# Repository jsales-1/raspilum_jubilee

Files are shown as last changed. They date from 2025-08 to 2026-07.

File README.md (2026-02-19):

## Science Jubilee

<p align="justify">
Science Jubilee é uma plataforma de automação laboratorial de código aberto, baseada no sistema Jubilee, uma plataforma de movimento multiferramenta extensível, originalmente projetada como uma impressora 3D com troca automática de cabeças de ferramenta <a href="https://jubilee3d.com/index.php?title=Main_Page">[1]</a>.
</p>

<p align="center">
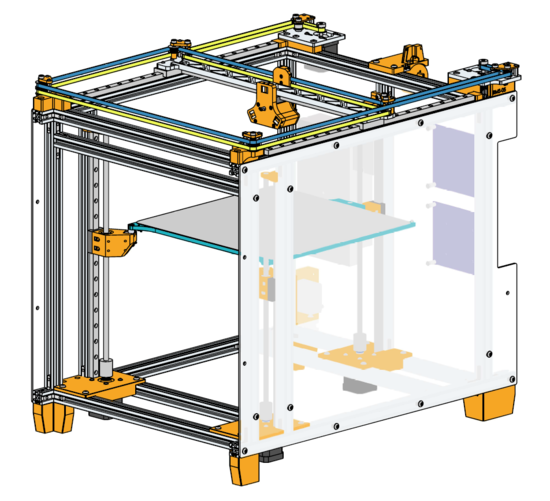
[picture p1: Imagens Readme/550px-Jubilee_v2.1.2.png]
  <br>
  <em>Figura 1 – Representação da estrutura da plataforma Jubilee 3D. </em>
</p>

<p align="justify">
A science-jubilee adapta essa infraestrutura para aplicações científicas, permitindo automação de experimentos com ferramentas como pipetas, câmeras, sondas e manuseio de amostras. A documentação oficial está disponível no site Science Jubilee Docs, que reúne guias de início rápido, construção da plataforma, desenvolvimento, referências da API e contribuições da comunidade. A plataforma é flexível e serve como base para diferentes aplicações de automação laboratorial, desde pipetagem e manipulação de amostras até aquisição de imagens. <a href="https://science-jubilee.readthedocs.io/en/latest/index.html">[2]</a>
</p>

### Experimentos da literatura que utilizaram a plataforma:

<p align="justify">
1. O artigo "A high-throughput workflow for the synthesis of CdSe nanocrystals using a sonochemical materials acceleration platform", publicado em 2023, apresenta uma plataforma aceleradora de materiais para síntese de nanocristais de CdSe. O sistema combinou o Jubilee com um equipamento de automação de líquidos da Opentrons OT-2, ultrassom e espectrometria, permitindo 625 condições experimentais testadas de forma automatizada <a href="https://pubs.rsc.org/en/content/articlehtml/2023/dd/d3dd00033h">[3]</a>.
</p>

<p align="center">
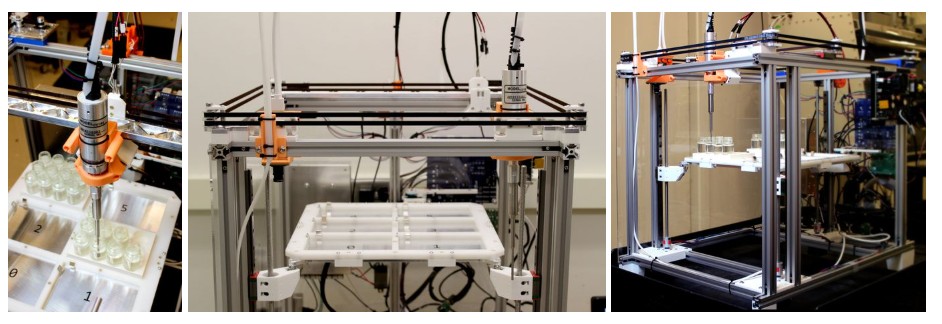
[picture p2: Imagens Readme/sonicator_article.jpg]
  <br>
  <em>Figura 2 – Plataforma de síntese de nanocristais com Jubilee 3D. </em>
</p>

<p align="justify">
2. O artigo "The Duckbot: A system for automated imaging and manipulation of duckweed" mostra um sistema para manipulação automatizada de lentilha d'água, uma planta que serve como modelo experimental. Foram implementadas ferramentas como pipeta, câmeras, loops de inoculação e módulos Python para controle via Jupyter notebooks, permitindo experimentos de crescimento com manipulação e análise automatizadas <a href="https://journals.plos.org/plosone/article?id=10.1371/journal.pone.0296717">[4]</a>.
</p>

<p align="center">
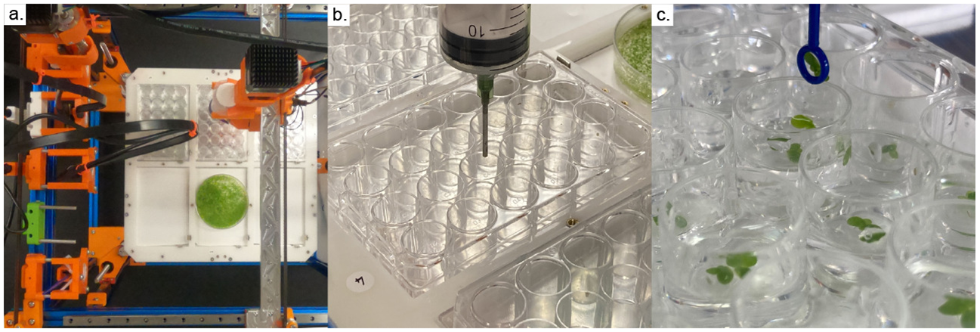
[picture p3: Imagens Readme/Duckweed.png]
  <br>
  <em>Figura 3 – Sistema Duckbot para experimentos com lentilha d'água. </em>
</p>

## Jubilee RaspIlum

<p align="justify">
O Jubilee RaspIlum é uma plataforma multifuncional para automação de experimentos na Ilum, montada como projeto de iniciação científica pelo aluno <a href="https://github.com/jsales-1)">José Sales</a>, da turma 23, sob a orientação do professor <a href="https://scholar.google.com.br/citations?user=yKskV5cAAAAJ&hl=pt-BR)">Dr. Amauri Jardim de Paula</a>. O projeto desenvolvido faz parte do INCT - Materials Informatics. 
</p>

<p align="center">
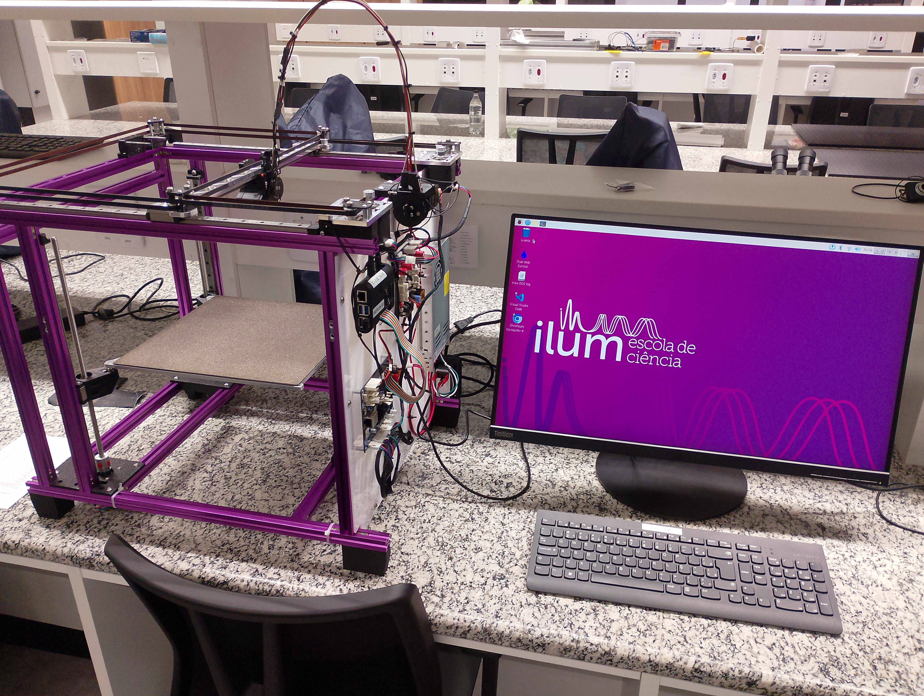
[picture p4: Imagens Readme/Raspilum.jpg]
  <br>
  <em>Figura 4 – Estrutura do Jubilee RaspIlum. </em>
</p>

### Estrutura

<p align="justify"> O Jubilee é construído com perfis de alumínio anodizado que formam a estrutura principal. Os eixos de movimento utilizam guias lineares, polias e correias dentadas para deslocamento em três dimensões. O volume útil de movimentação é de aproximadamente 330 mm × 350 mm × 300 mm. A base é sustentada por três fusos acionados por motores de passo independentes, que realizam o nivelamento automático e a correção de inclinações da mesa. O peso total do sistema é de cerca de 20 kg. É possível conferir as etapas de montagem do sistema pelo manual oferecido no site do Jubilee 3D <a href="https://www.jubilee3d.com/index.php?title=Assembly_Instructions">[5]</a>. O Github do Science Jubilee também disponibiliza modelos 3D de ferramentas e componentes da estrutura do Jubilee, o que facilita a manutenção da máquina e criação de novas funcionalidades. <a href = https://github.com/machineagency/science-jubilee/tree/main>[6]</a>.
</p>
  
### Componentes elétricos/mecânicos

<p align="justify">
A Jubilee RaspIlum se movimenta por meio de 5 motores de passo, sendo 2 para XY e 3 para Z. Há também um sexto motor para o trocador de ferramentas, denominado eixo U. Os motores são controlados através de uma Duet Mini e sua placa de extensão, as quais são tipicamente utilizadas para controle de máquinas CNC e impressoras 3D, recebendo G-Code e realizando as operações <a href="https://www.jubilee3d.com/index.php?title=Assembly_Instructions">[5]</a> <a href="https://docs.duet3d.com/Duet3D_hardware/Duet_3_family/Duet_3_Mini_5+_Hardware_Overview">[7]</a>. Com essas duas placas, temos 8 drivers para controle de motores de passo, havendo atualmente 6 ocupados. Diferentemente do planejado para impressoras 3D, não utilizamos sistema de aquecimento de superfície na Jubilee RaspIlum.
Na imagem a seguir, é possível conferir o painel de controle do Jubilee RaspIlum.</p>

<p align="center">
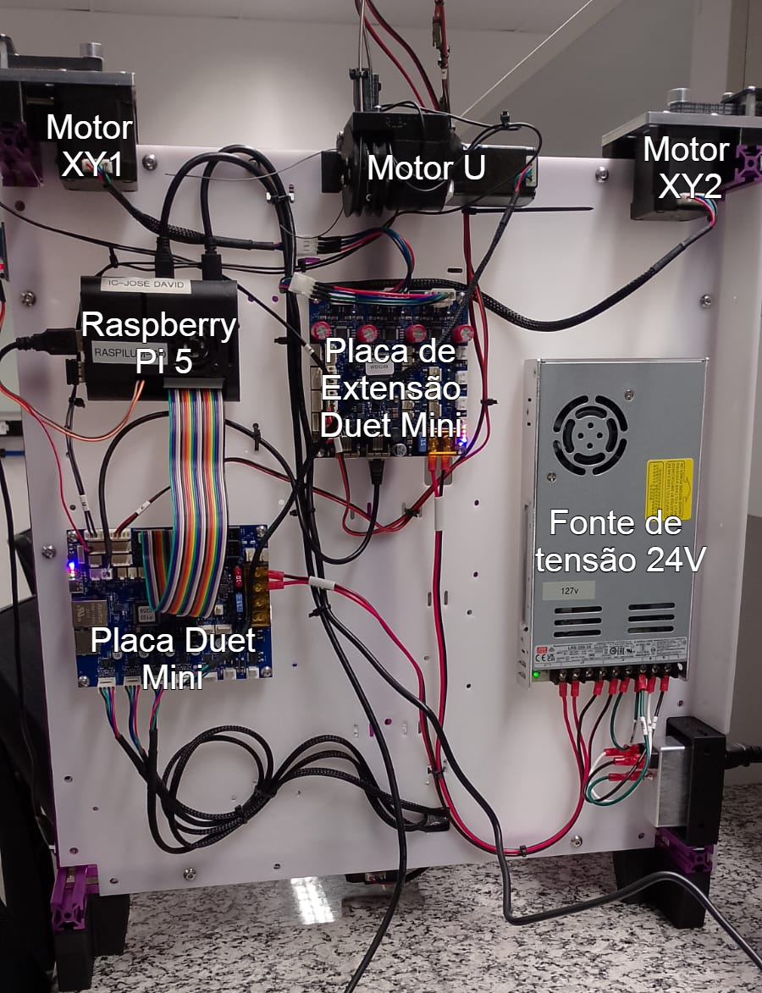
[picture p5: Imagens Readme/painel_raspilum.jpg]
  <br>
  <em>Figura 5 – Painel de controle do Jubilee 3D</em>
</p>

<p align='justify'>
Esse painel é exposto para que seja possível mudar conexões e implementar novas funcionalidades com maior facilidade. Pode-se observar a fonte de alimentação, as duas placas de controle dos motores, a placa Raspberry conectada à placa principal por um cabo flat de 26 vias, e os motores XY e U. É importante ressaltar que os motores XY operam em conjunto: a definição do eixo que está sendo seguido depende do sentido de rotação desses motores. Se ambos, por exemplo, estiverem rotacionando em sentido horário, o carregador de ferramentas se move apenas no eixo X. As conexões com as placas de controle não abrangem apenas os motores, mas também os sensores de fim de curso, que servem para fazer a calibração do sistema. No esquemático a seguir é possível conferir, em mais detalhes, a conexão dos sensores de fim de curso e dos motores nos drivers e pinos I/O das placas Duet Mini com sua placa de extensão.
</p>

<p align="center">
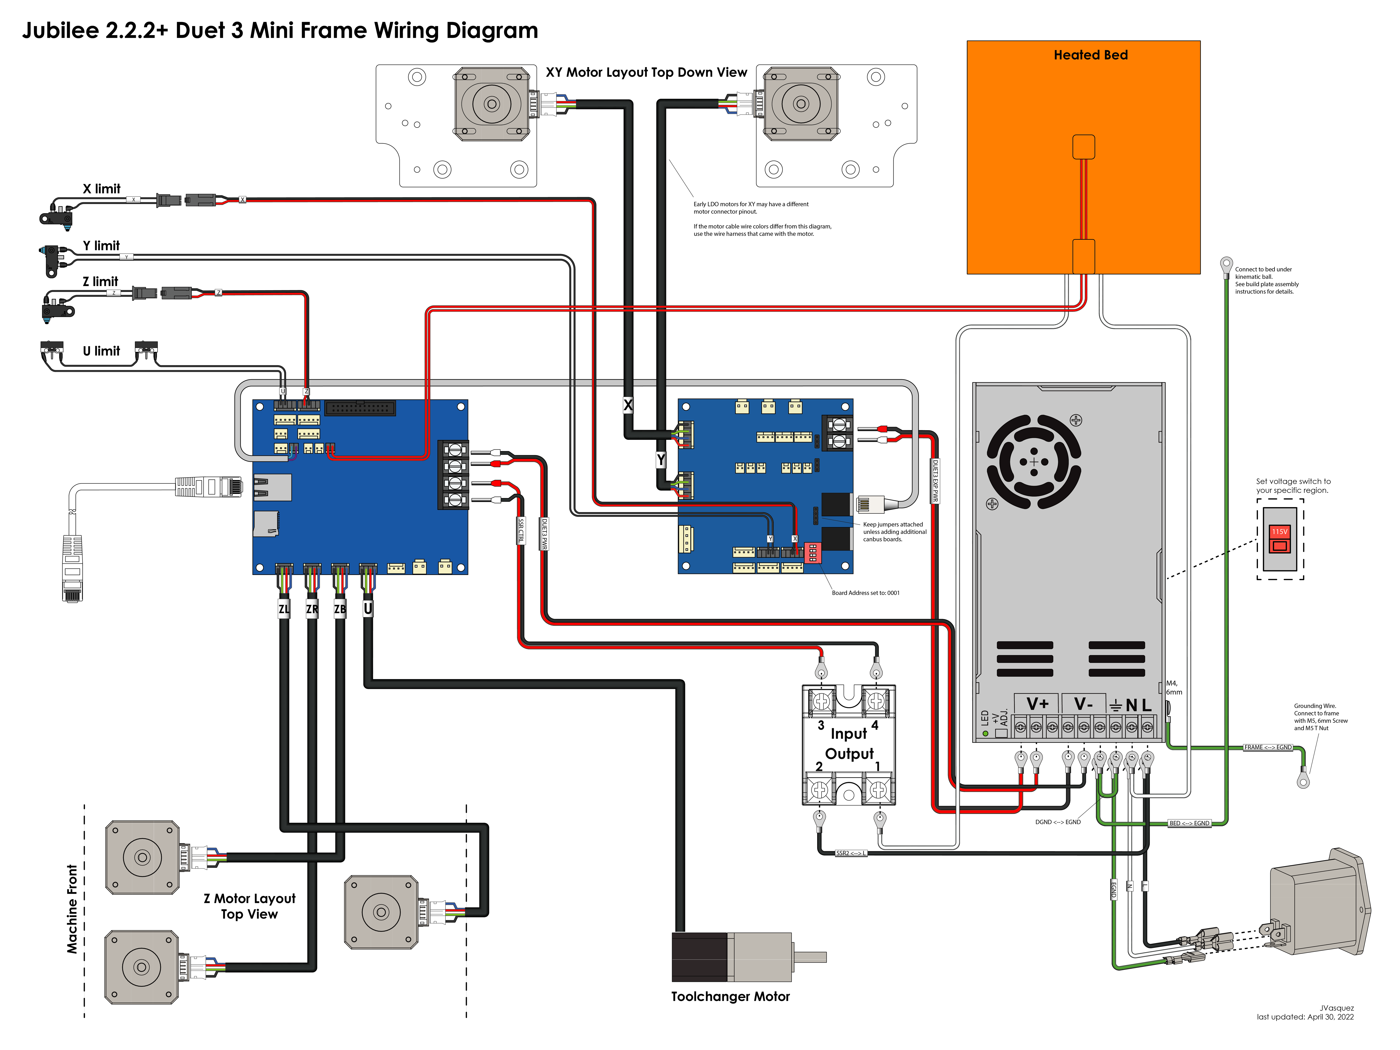
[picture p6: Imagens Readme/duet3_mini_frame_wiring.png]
  <br>
  <em>Figura 6 – Esquemático de conexões da Duet Mini</em>
</p>

### Sistema de troca de ferramentas
<p align="justify">
O Jubilee 3D possui um sistema para acoplar e desacoplar ferramentas. Esse sistema consiste em um eixo feito para entrar dentro de uma peça chamada "<i>wegde plate</i> e rotacionar, o que impede que ele possa sair. A rotação desse eixo é controlada pelo motor U.
Todas as ferramentas planejadas para o sistema devem possuir "<i>wegde plate</i> para que seja possível a acoplar e desacoplar no carregador de ferramentas.
</p>

<p align="center">
  <br>
  <em>Figura 7 – Eixo de troca de ferramentas.</em>
</p>

### Software

<p align="justify">
Para criar uma interface mais simplificada e acessível, uma placa Raspberry Pi 5 é utilizada como Single Board Computer, permitindo que o sistema seja controlado por um servidor local ou por linguagem Python. O Raspberry roda o sistema operacional Raspberry Pi OS, possui 8 GB de RAM e cerca de 128 GB de memória disponível. É executado no Raspberry o Duet Software Framework (DSF), que conecta a placa ao Duet 3, envia comandos G-Code e controla motores, sensores e ferramentas da máquina. A instalação foi feita seguindo o protocolo disponível no site da Duet 3D <a href="https://docs.duet3d.com/User_manual/Machine_configuration/SBC_setup">[8]</a>. Para utilizar o Python nesse subsistema Linux, foi necessário instalar uma versão do Anaconda específica para Raspberry Pi, através do GitHub Miniforge <a href="https://github.com/conda-forge/miniforge">[9]</a>
</p>

## Uso do Jubilee RaspIlum

### 1. Ligando o sistema
<p align = 'justify'> Para ligar o sistema, é necessário ligar primeiro o Raspberry, pressionando o botão presente nele, e em seguida ligar as placas Duet, acionando o chave que ativa a fonte de alimentação. A Figura 8 mostra o a posição do botão para ligar o Raspberry, na esquerda, e a chave para ligar o Duet, na direita.  </p>
<p align="center">
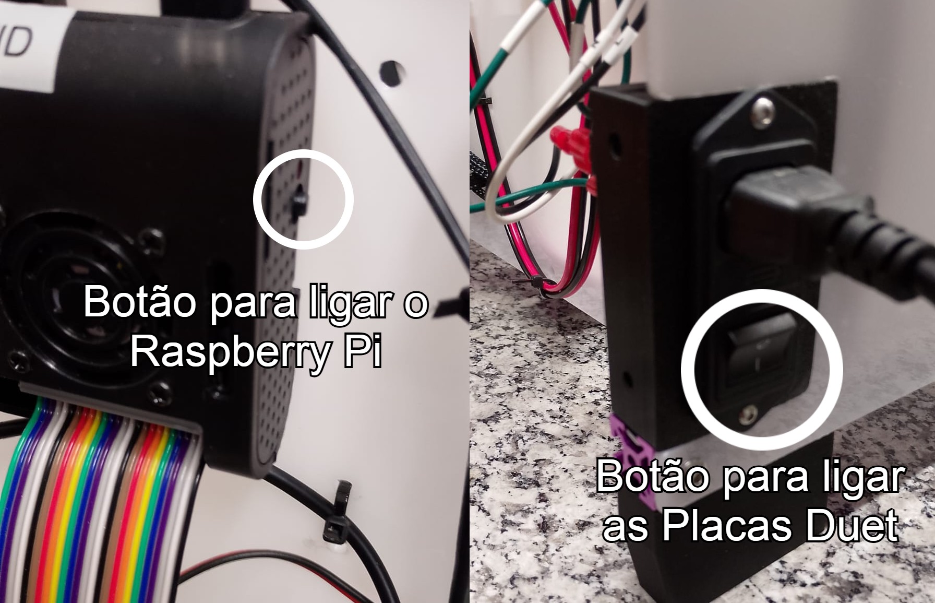
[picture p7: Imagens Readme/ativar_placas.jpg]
  <br>
  <em>Figura 8 - Locais para ativação das placas de controle.</em>
</p>    
<p align = 'justify'> Ao ligar o Raspberry, ele funcionará como um desktop normal, exibindo sua interface no monitor e podendo ser controlado por mouse/teclado. Apesar de ser uma imagem baseada em Linux, o sistema é bem amigável e intuitivo. A depender a forma com que o Raspberry foi desligado anteriormente, ele também pode pedir uma senha de usuário ao ser novamente ligado, que no caso é "amauras". </p>

<h3>2. Controlando por Python</h3>

<p align="justify">
Entre no VSCode e abra a pasta <code>Documentos/IC/raspilum_jubilee</code>. Esse caminho é referente ao repositório que você está acessando agora. Dentro dela, acesse a pasta <code>Controle_jubilee3d</code> e confira os scripts Python que realizam o controle da máquina e das ferramentas, assim como as pastas com testes e experimentos.  

Para fazer um <i>Quick Start</i>, abra os notebooks disponíveis em <code>Exemplos de uso/</code>. O arquivo <code>1 - Movimentando Jubilee.ipynb</code> contém exemplos básicos de controle de movimentação da plataforma via envio de comandos e definição de posições. Já o arquivo <code>2 - Utilizando Ferramentas.ipynb</code> apresenta as classes desenvolvidas para o controle das diferentes ferramentas acopláveis, demonstrando como instanciá-las, configurar seus parâmetros e utilizar seus métodos específicos.

O arquivo <code>jubilee_controller.py</code> é completamente baseado no arquivo de mesmo nome presente no repositório do Science Jubilee <a href = https://github.com/machineagency/science-jubilee/tree/main>[6]</a>. Esse arquivo é o mais importante para o projeto, pois é responsável por gerar a interface python/G-Code. De forma resumida, o objeto que representa a máquina é criada nesse arquivo e, utilizando de uma comunicação com o servidor local, é possível enviar os comandos G-Code ativando métodos específicos do objeto JubileeController. 

A seguir, você pode ver a árvore de diretórios desse diretório.
</p>

<pre>
raspilum_jubilee3d/
├── Controle_jubilee3d/
│   ├── __pycache__/
│   ├── Exemplos de uso/
│   │   ├── 1 - Movimentando Jubilee.ipynb      # Quick Start com exemplos de códigos para movimentação
│   │   └── 2 - Utilizando Ferramentas.ipynb    # Expicação das classes de ferramentas e seus métodos
│   ├── Experimento 0 - Perda de Precisão XY/
│   ├── Experimento 1 - Crescimento Leveduras/
│   ├── Experimento 2 - Síntese de nanorods de ouro/
│   ├── Experimento 3 - DipCoating/
│   ├── Experimento 4 - Síntese de nanopartículas/
│   ├── Testes de Ferramentas/
│   ├── camera_circle_detect.py
│   ├── camera_controller.py
│   ├── camera.py
│   ├── gripper_controller.py
│   ├── image_processing.py
│   ├── jubilee_controller.py
│   ├── magnetic_stirrer_control.py
│   ├── micropipette_controller.py
│   ├── operacoes_iniciais.ipynb
│   └── temperature.py
│
├── Imagens Readme/
├── Jubilee Gcode/
├── Peças stl/
├── .gitignore
└── README.md
</pre>

<h3>2.1. Controlando por interface do servidor local</h3>

<p align = 'justify'>Abra o navegador Chromium e acesse http://jubilee.local/. A página exibida é a interface web do Duet Web Control, que já vem incluida na imagem do sistema operacional fornecida para o Raspberry Pi <a href="https://docs.duet3d.com/User_manual/Machine_configuration/SBC_setup">[8]</a>.
Na tela inicial aparecem painéis com status dos eixos, leitura de sensores e console para envio de G-Code; o Machine Control, que permite a movimentação manual dos eixos, troca de ferramentas e homing; Settings: ajustes de rede, firmware e parâmetros de movimento
Essa interface, exibida na Figura 9, permite controle completo sem necessidade de scripts Python. Funciona muito bem para testes rápidos, calibração e operação básica da Jubilee RaspIlum.</p> 
<p align="center">
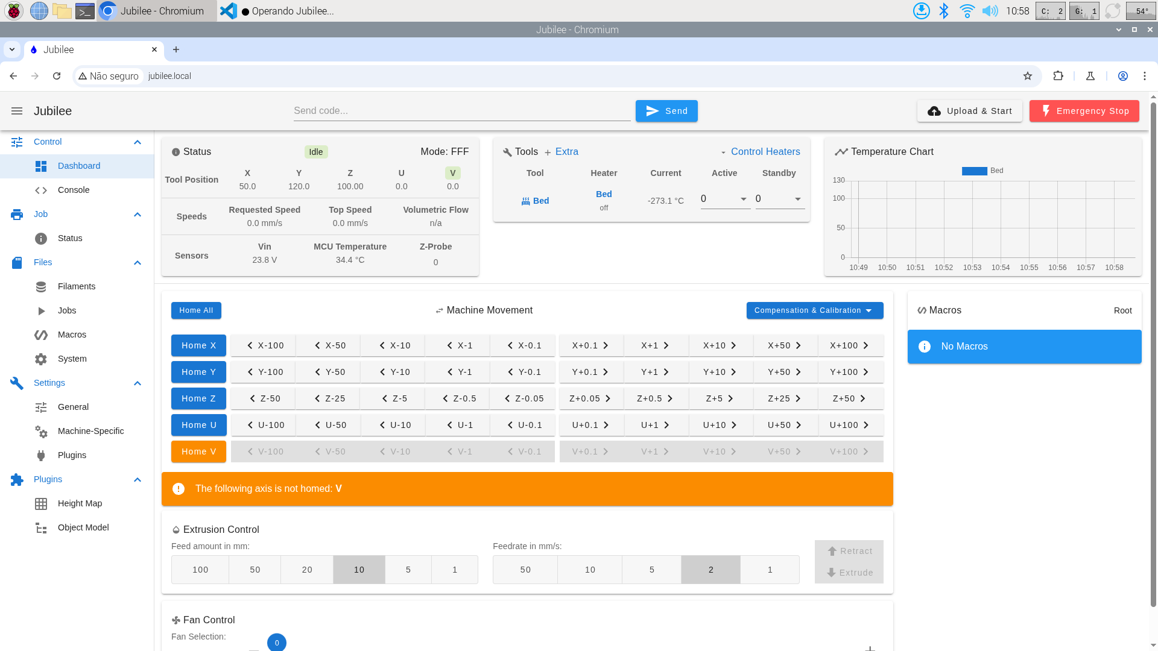
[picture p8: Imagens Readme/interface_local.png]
  <br>
  <em>Figura 9 – Interface Web do Duet Web Control.</em>
</p>

## Ferramentas implementadas.

### Câmera</i>

<p align='justify'>A câmera USB instalada como ferramenta possui uma resolução de 5MP e é acessada através da biblioteca <i>python</i> <i>openCV</i>. Conferindo a árvores de arquivos do repositório, pode-se notar que há três arquivos com o palavra "camera". O arquivo <code>camera_controller.py</code> é responsável por gerenciar a câmera enquanto ferramenta do Jubilee RaspIlum, permitindo instalar e desinstalar a câmera, além de capturar imagens quando necessário. O arquivo <code>camera.py</code> mantém o vídeo da câmera ativo em uma janela separada, o que é útil para ajustes de foco e enquadramento antes de iniciar experimentos. O <code>camera_circle.py</code> aplica um algoritmo de detecção de círculos sobre o vídeo, mas essa funcionalidade é apenas um teste de processamento de imagem e não é importante para o uso da câmera na plataforma. </p>

<p align="center">
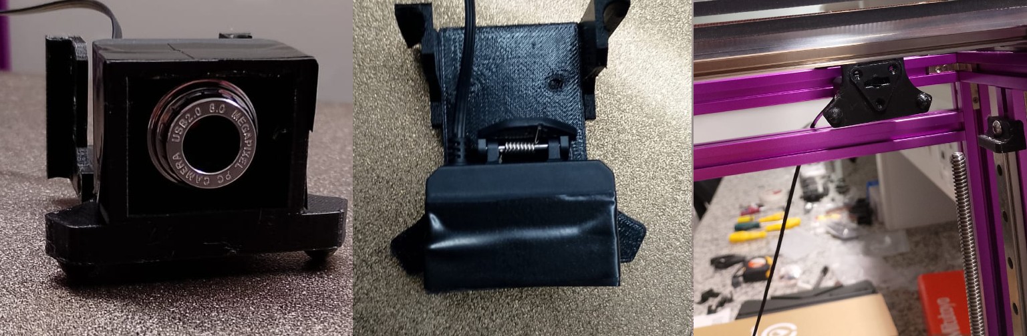
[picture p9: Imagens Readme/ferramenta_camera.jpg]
  <br>
  <em>Figura 10 – Câmera USB vista em diferentes posições.</em>
</p>

### Gripper
<p align='justify'>
O gripper é uma ferramenta de manipulação mecânica, projetada para pegar, transportar e soltar amostras leves. O gripper utiliza um servo SG9 conectado diretamente aos pinos GPIO do Raspberry, o que limita a carga que ele consegue suportar. Apesar disso, é adequado para segurar lâminas, por exemplo, em experimentos de <i>dip coating</i>. O design ainda está em desenvolvimento e melhorias futuras visam aumentar a força e a precisão da ferramenta através da susbtituição do motor utilizado. </p>

<p align="center">
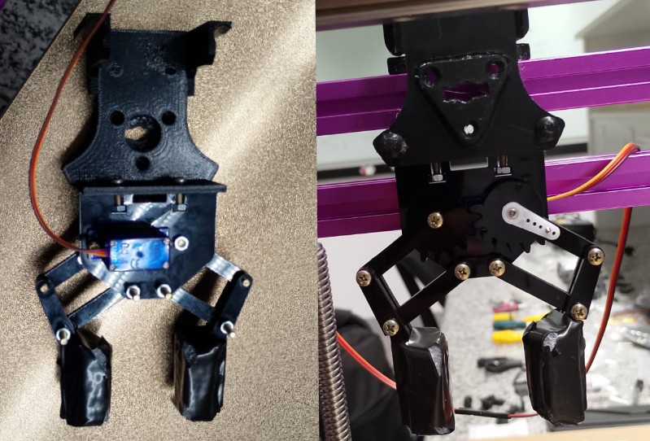
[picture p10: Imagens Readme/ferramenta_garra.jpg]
  <br>
  <em>Figura 11 – Gripper visto de diferentes posições.</em>
</p>

### Micropipetadora Automática
<p align='justify'>
A micropipetadora automática é a ferramenta responsável pela manipulação volumétrica de líquidos na plataforma Jubilee RaspIlum. É uma micropipetadora elétrica da Opentrons, a qual foi integrada mecanicamente à estrutura do sistema. Seu acionamento é realizado por meio de um motor de passo conectado a um dos drivers da placa Duet, ele permite controlar eletronicamente o deslocamento do êmbolo e consequentemente os volumes aspirados e dispensados.
</p>

 </p>

<p align="center">
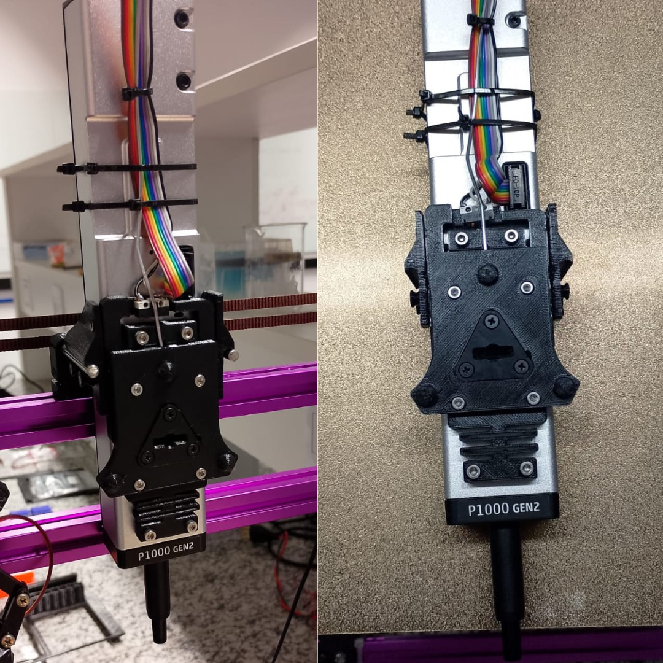
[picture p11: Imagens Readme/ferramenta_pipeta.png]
  <br>
  <em>Figura 12 – Micropipetaadora vista em diferentes posições.</em>
</p>

## Referências      

<p align="justify">
[1] Jubilee 3D. Jubilee wiki. Disponível em: https://jubilee3d.com/index.php?title=Main_Page <br>
[2] Science Jubilee. Documentation. Disponível em: https://science-jubilee.readthedocs.io/en/latest/index.html <br>
[3] Telford J, Newton G, Shields R, Mohr S, Handley J, Thielbeer F, et al. A sonochemical materials acceleration platform for the synthesis of CdSe nanocrystals. Digital Discovery. 2023;2(3):856-865. <br>
[4] Babl L, Holten V, Reuter M, Schoof H. Duckbot: a modular open-source platform for automated experiments with duckweed. PLoS One. 2024;19(2):e0296717. <br>
[5] Jubilee 3D. Assembly Instructions. Disponível em: https://www.jubilee3d.com/index.php?title=Assembly_Instructions <br>
[6] MACHINEAGENCY. GitHub - machineagency/science-jubilee: Controlling Jubilees for Science! Disponível em: <https://github.com/machineagency/science-jubilee/tree/main>. <br>
[7] DUET3D. Duet 3 Mini 5+ Hardware Overview. 2025. Disponível em: https://docs.duet3d.com/Duet3D_hardware/Duet_3_family/Duet_3_Mini_5%2B_Hardware_Overview <br>
[8] Duet 3D. SBC Setup. Disponível em: https://docs.duet3d.com/User_manual/Machine_configuration/SBC_setup <br>
[9] conda-forge/miniforge. Disponível em: https://github.com/conda-forge/miniforge
</p>

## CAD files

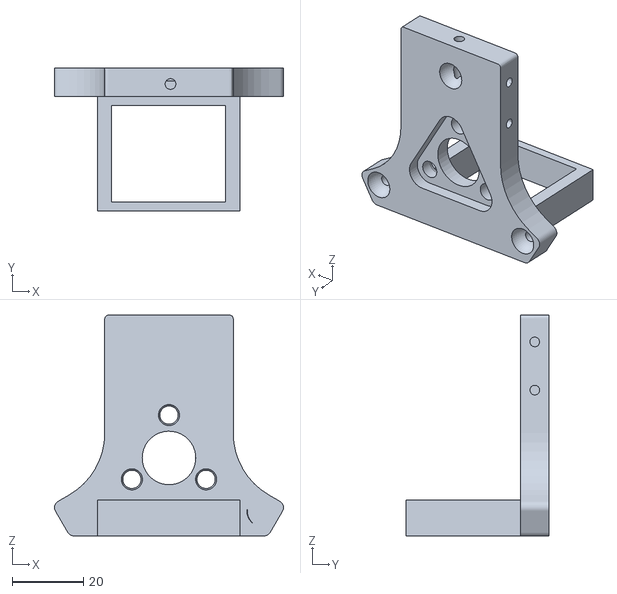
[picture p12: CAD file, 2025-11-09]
Peças stl/Câmera/Suporte Ferramenta Câmera.stl
64.1 x 40.1 x 61.8

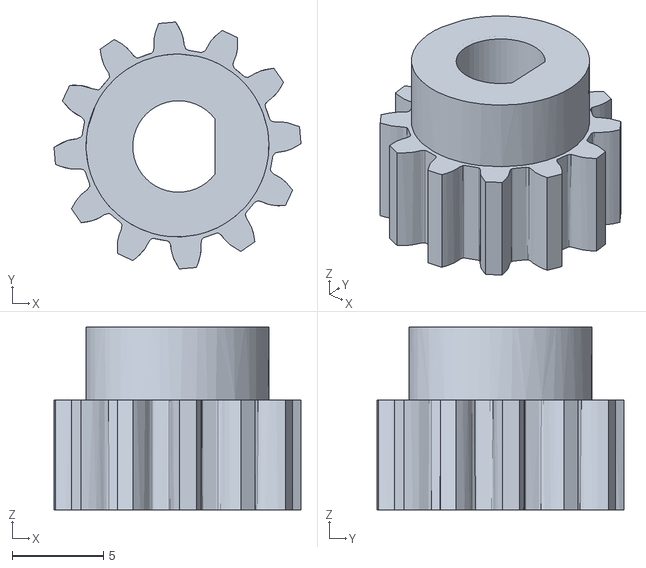
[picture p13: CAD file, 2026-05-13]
Peças stl/Gripper/Gear.stl
13.5 x 13.5 x 10.0

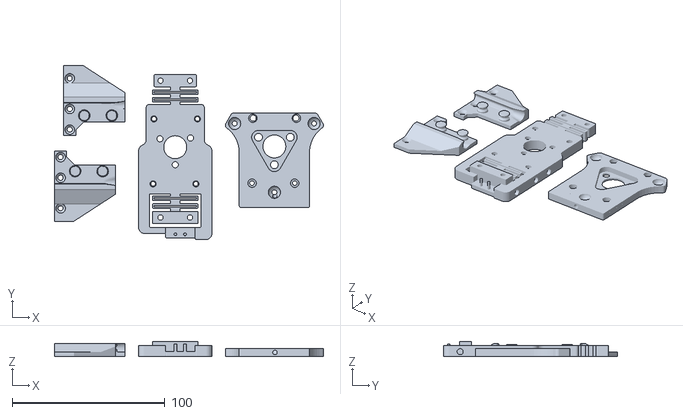
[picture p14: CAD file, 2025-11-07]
Peças stl/Micropipetadora/Suporte Ferramenta Micropipetadora.stl
176.0 x 114.0 x 9.50

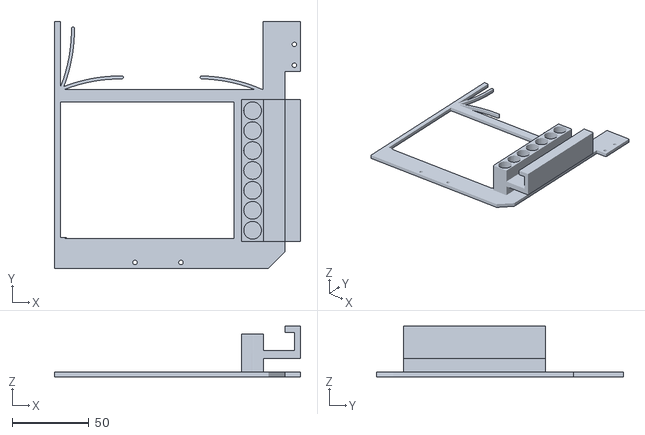
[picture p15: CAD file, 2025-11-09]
Peças stl/Suporte de Base/Suporte Eppendorf Base.stl
160.5 x 161.3 x 33.0

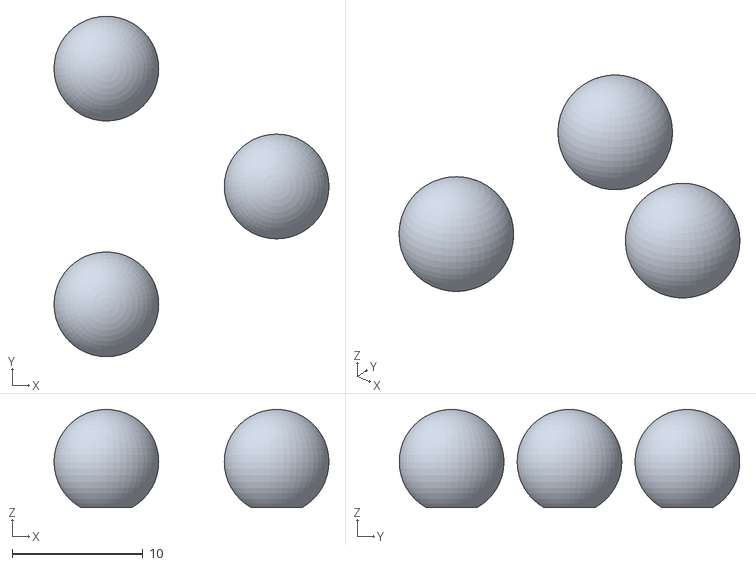
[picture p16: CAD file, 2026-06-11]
Peças stl/Universal/Esferas de suporte.stl
21.0 x 26.0 x 7.50

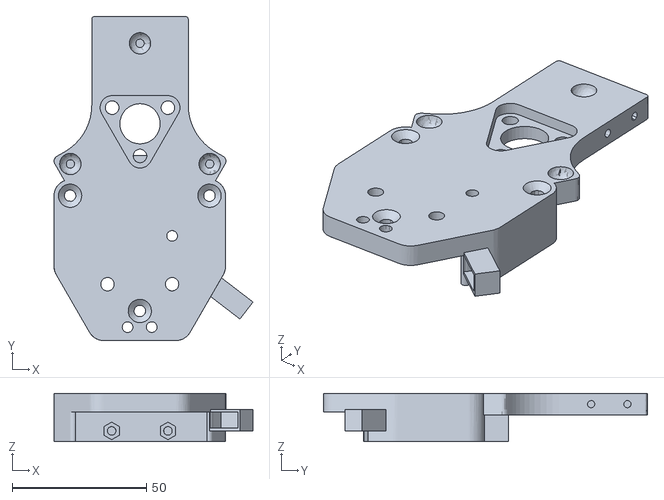
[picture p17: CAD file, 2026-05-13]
Peças stl/Gripper/Base_inferior.stl
74.2 x 120.8 x 18.0

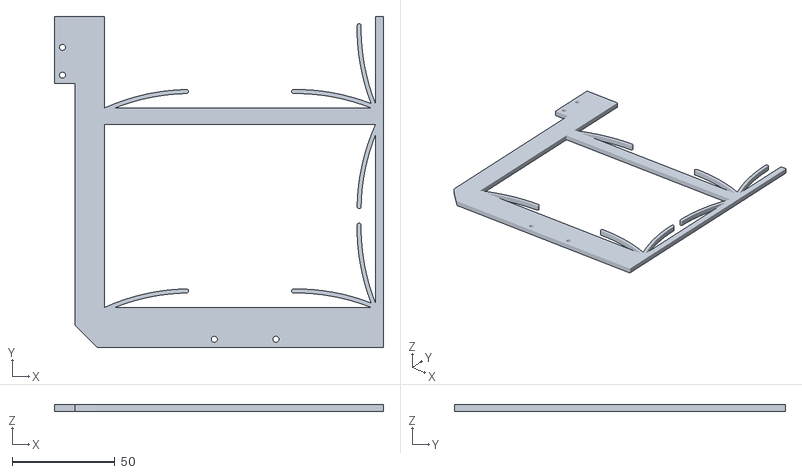
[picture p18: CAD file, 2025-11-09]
Peças stl/Suporte de Base/Suporte Base.stl
160.5 x 161.3 x 3.18

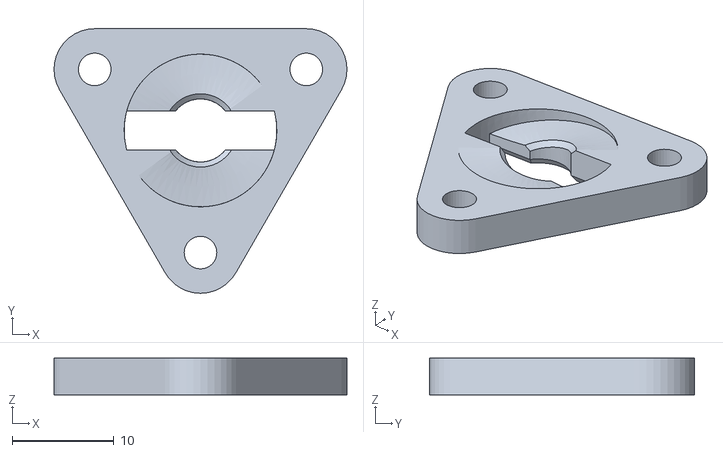
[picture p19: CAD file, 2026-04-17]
Peças stl/Universal/Conector de Eixo.STL
28.8 x 26.0 x 3.60

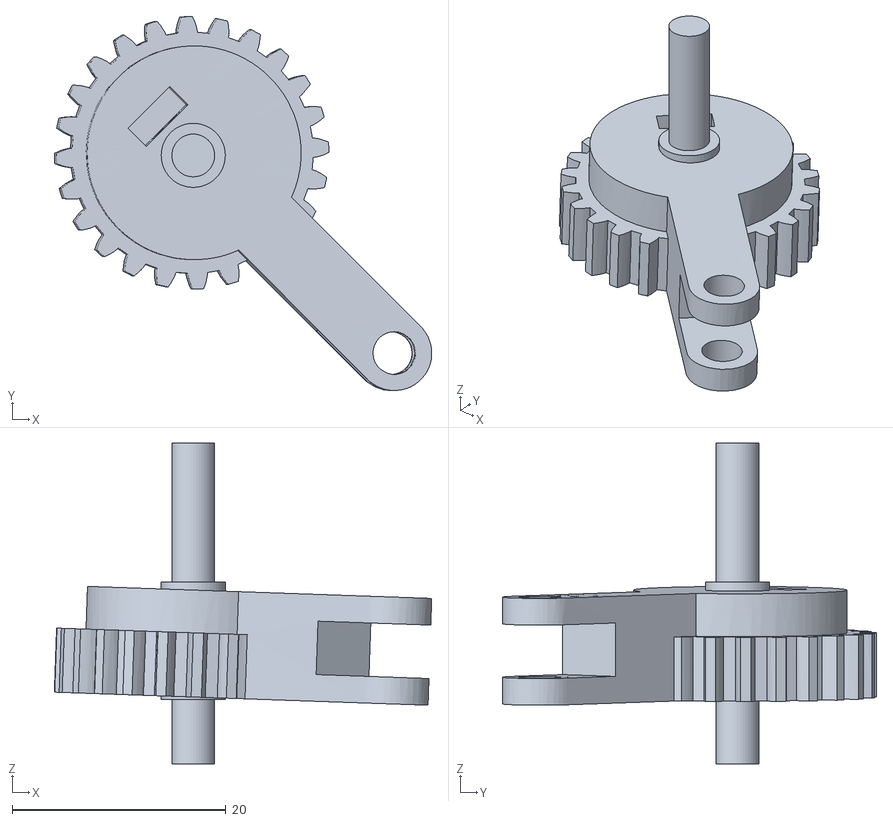
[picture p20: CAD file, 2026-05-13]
Peças stl/Gripper/Gear2.stl
35.3 x 35.0 x 30.0

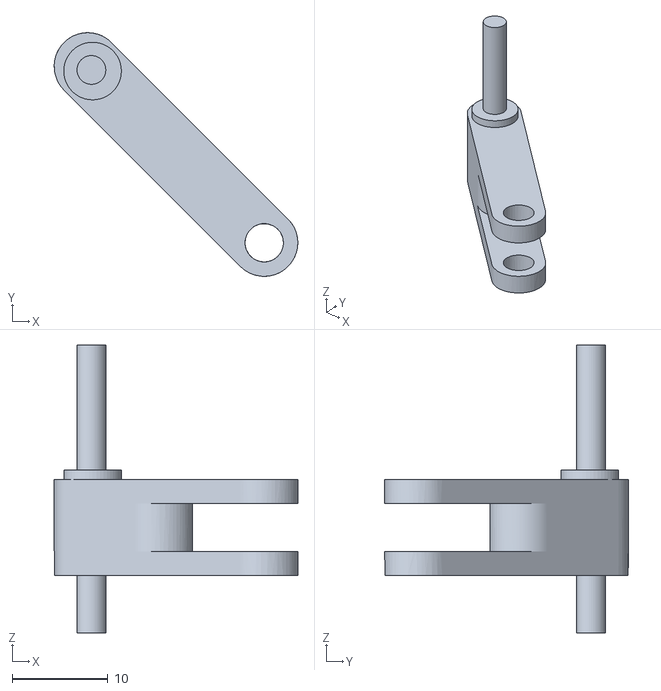
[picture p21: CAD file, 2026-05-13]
Peças stl/Gripper/biceps.stl
25.4 x 25.4 x 30.0

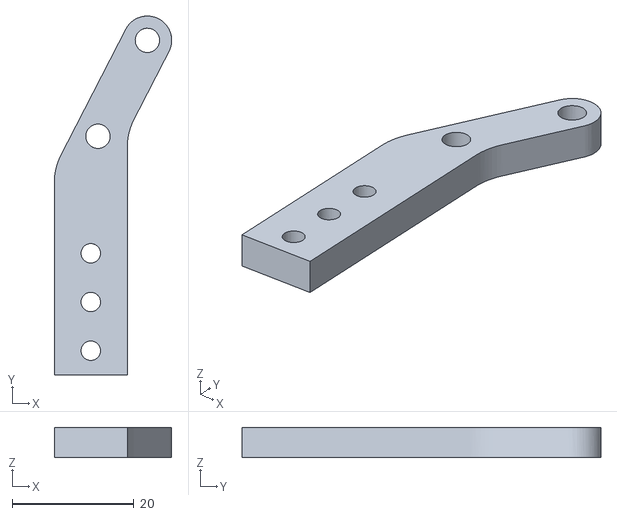
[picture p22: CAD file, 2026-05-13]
Peças stl/Gripper/antebraco.stl
19.3 x 59.0 x 5.00

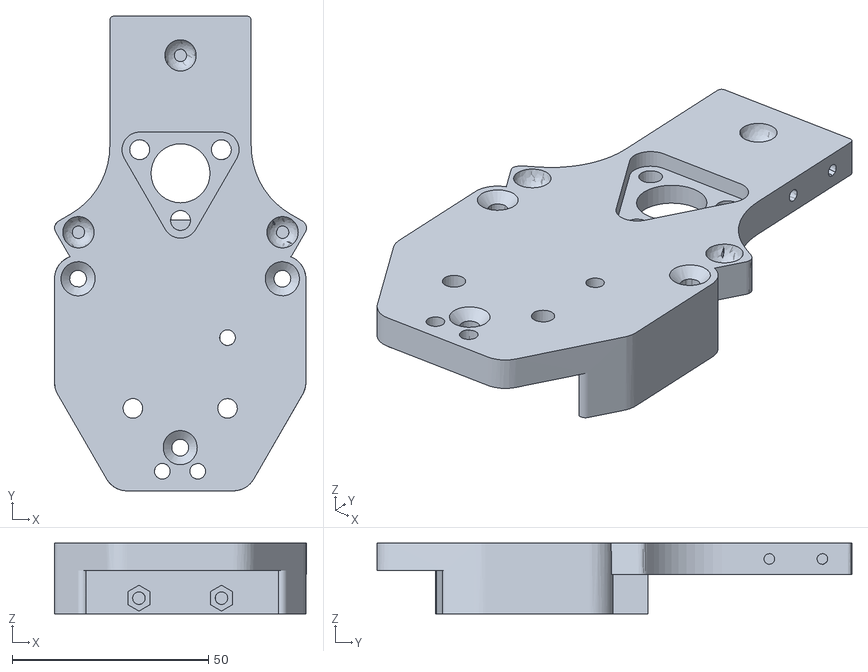
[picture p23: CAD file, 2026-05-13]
Peças stl/Gripper/Base_superior.stl
64.1 x 120.8 x 18.0

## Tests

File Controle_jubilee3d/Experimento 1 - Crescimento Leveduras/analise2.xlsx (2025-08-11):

 | Temperatura (°C) | Umidade (%) | Hora
0 | 21.4 | 49 | 08/08/25 10:39:18
1 | 23 | 47 | 08/08/25 11:09:48
2 | 23.5 | 45 | 08/08/25 11:40:19
3 | 24.1 | 44 | 08/08/25 12:10:49
4 | 24.5 | 42 | 08/08/25 12:41:19
5 | 24.8 | 41 | 08/08/25 13:11:50
6 | 25.8 | 38 | 08/08/25 13:42:20
7 | 25.8 | 37 | 08/08/25 14:12:50
8 | 25.8 | 36 | 08/08/25 14:43:21
9 | 25.8 | 38 | 08/08/25 15:13:51
10 | 25.8 | 38 | 08/08/25 15:44:21
11 | 25.3 | 39 | 08/08/25 16:14:52
12 | 25.3 | 42 | 08/08/25 16:45:22
13 | 25.3 | 45 | 08/08/25 17:15:52
14 | 24.8 | 47 | 08/08/25 17:46:23
15 | 24.8 | 47 | 08/08/25 18:16:53
16 | 24.5 | 49 | 08/08/25 18:47:24
17 | 24.1 | 49 | 08/08/25 19:17:54
18 | 24.1 | 48 | 08/08/25 19:48:24
19 | 24.1 | 48 | 08/08/25 20:18:55
20 | 24.1 | 48 | 08/08/25 20:49:25
21 | 24.1 | 48 | 08/08/25 21:19:55
22 | 23.3 | 55 | 08/08/25 21:50:26
23 | 23 | 55 | 08/08/25 22:20:56
24 | 23 | 55 | 08/08/25 22:51:26
25 | 22.6 | 56 | 08/08/25 23:21:57
26 | 22.6 | 57 | 08/08/25 23:52:27
27 | 22.2 | 58 | 08/09/25 00:22:57
28 | 22.2 | 58 | 08/09/25 00:53:28
29 | 22.2 | 58 | 08/09/25 01:23:58
30 | 21.8 | 58 | 08/09/25 01:54:28
31 | 21.8 | 59 | 08/09/25 02:24:59
32 | 21.8 | 59 | 08/09/25 02:55:29
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

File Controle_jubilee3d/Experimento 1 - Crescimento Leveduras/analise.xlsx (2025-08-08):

 | Temperatura (°C) | Umidade (%) | Hora
0 | 21 | 39 | 08/04/25 15:20:25
1 | 23.8 | 36 | 08/04/25 15:50:56
2 | 24.1 | 35 | 08/04/25 16:21:26
3 | 23.8 | 35 | 08/04/25 16:51:57
4 | 23.8 | 34 | 08/04/25 17:22:27
5 | 23.8 | 34 | 08/04/25 17:52:57
6 | 23.8 | 35 | 08/04/25 18:23:28
7 | 23.8 | 35 | 08/04/25 18:53:58
8 | 23.4 | 36 | 08/04/25 19:24:28
9 | 23 | 36 | 08/04/25 19:54:59
10 | 23 | 37 | 08/04/25 20:25:29
11 | 22.6 | 37 | 08/04/25 20:55:59
12 | 22.6 | 38 | 08/04/25 21:26:30
13 | 22.6 | 38 | 08/04/25 21:57:00
14 | 22.6 | 40 | 08/04/25 22:27:30
15 | 22.6 | 45 | 08/04/25 22:58:01
16 | 22.2 | 48 | 08/04/25 23:28:31
17 | 22.2 | 49 | 08/04/25 23:59:02
18 | 21.8 | 49 | 08/05/25 00:29:32
19 | 21.8 | 49 | 08/05/25 01:00:02
20 | 21.4 | 49 | 08/05/25 01:30:33
21 | 21.4 | 49 | 08/05/25 02:01:03
22 | 21.4 | 49 | 08/05/25 02:31:33
23 | 21 | 49 | 08/05/25 03:02:04
24 | 21 | 49 | 08/05/25 03:32:34
25 | 20.6 | 49 | 08/05/25 04:03:05
26 | 20.6 | 49 | 08/05/25 04:33:35
27 | 20.6 | 49 | 08/05/25 05:04:05
28 | 20.3 | 49 | 08/05/25 05:34:36
29 | 20.6 | 49 | 08/05/25 06:05:06
30 | 20.6 | 49 | 08/05/25 06:35:36
31 | 20.2 | 50 | 08/05/25 07:06:07
32 | 20.2 | 50 | 08/05/25 07:36:37
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

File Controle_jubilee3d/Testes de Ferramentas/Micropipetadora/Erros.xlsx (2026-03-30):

Volume Desejado (µL) | Média dos volumes obtidos (µL) | Erro Relativo (%) | Erro Absoluto (µL)
100 | 100.133735 | 1.33316 | 1.33316
120 | 120.361083 | 1.294879 | 1.553855
200 | 201.604814 | 0.448559 | 0.897119
300 | 300.066867 | 0.714469 | 2.143406
500 | 499.665664 | 0.234513 | 1.172563
1000 | 999.832832 | 0.098615 | 0.986151

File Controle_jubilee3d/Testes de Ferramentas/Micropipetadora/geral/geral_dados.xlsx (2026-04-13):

Peso (g) | Peso com líquido (g) | Valor teórico | Peso água (g) | Volume experimental (µL) | Erro absoluto (µL) | Erro relativo (%)
2.13 | 2.23 | 100 | 0.10 | 105.32 | 5.32 | 5.32
2.17 | 2.28 | 100 | 0.10 | 104.31 | 4.31 | 4.31
2.13 | 2.24 | 100 | 0.10 | 104.31 | 4.31 | 4.31
2.16 | 2.26 | 100 | 0.10 | 100.30 | 0.30 | 0.30
2.23 | 2.33 | 100 | 0.10 | 101.30 | 1.30 | 1.30
2.27 | 2.37 | 100 | 0.10 | 101.30 | 1.30 | 1.30

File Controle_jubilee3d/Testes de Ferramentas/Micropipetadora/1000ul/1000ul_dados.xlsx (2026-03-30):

Peso (g) | Peso com líquido (g) | Valor teórico | Peso água (g) | Volume experimental (µL) | Erro absoluto (µL) | Erro relativo (%)
2.124 | 3.12 | 1000 | 0.996 | 998.996991 | 1.003009027 | 0.1003009027
2.124 | 3.121 | 1000 | 0.997 | 1000 | 1.136868377e-13 | 1.136868377e-14
2.124 | 3.122 | 1000 | 0.998 | 1001.003009 | 1.003009027 | 0.1003009027
2.124 | 3.12 | 1000 | 0.996 | 998.996991 | 1.003009027 | 0.1003009027
2.124 | 3.122 | 1000 | 0.998 | 1001.003009 | 1.003009027 | 0.1003009027
2.124 | 3.12 | 1000 | 0.996 | 998.996991 | 1.003009027 | 0.1003009027

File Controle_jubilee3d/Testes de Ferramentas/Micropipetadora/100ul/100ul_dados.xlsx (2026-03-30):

Peso (g) | Peso com líquido (g) | Valor teórico | Peso água (g) | Volume experimental (µL) | Erro absoluto (µL) | Erro relativo (%)
2.124 | 2.225 | 100 | 0.101 | 101.3039117 | 1.303911735 | 1.303911735
2.124 | 2.225 | 100 | 0.101 | 101.3039117 | 1.303911735 | 1.303911735
2.124 | 2.223 | 100 | 0.099 | 99.29789368 | 0.702106319 | 0.702106319
2.124 | 2.225 | 100 | 0.101 | 101.3039117 | 1.303911735 | 1.303911735
2.124 | 2.223 | 100 | 0.099 | 99.29789368 | 0.702106319 | 0.702106319
2.124 | 2.222 | 100 | 0.098 | 98.29488465 | 1.705115346 | 1.705115346

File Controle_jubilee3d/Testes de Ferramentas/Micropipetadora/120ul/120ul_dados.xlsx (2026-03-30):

Peso (g) | Peso com líquido (g) | Valor teórico | Peso água (g) | Volume experimental (µL) | Erro absoluto (µL) | Erro relativo (%)
2.124 | 2.246 | 120 | 0.122 | 122.3671013 | 2.367101304 | 1.97258442
2.124 | 2.245 | 120 | 0.121 | 121.3640923 | 1.364092277 | 1.136743564
2.124 | 2.245 | 120 | 0.121 | 121.3640923 | 1.364092277 | 1.136743564
2.124 | 2.243 | 120 | 0.119 | 119.3580742 | 0.6419257773 | 0.5349381478
2.124 | 2.242 | 120 | 0.118 | 118.3550652 | 1.644934804 | 1.370779004
2.124 | 2.243 | 120 | 0.119 | 119.3580742 | 0.6419257773 | 0.5349381478

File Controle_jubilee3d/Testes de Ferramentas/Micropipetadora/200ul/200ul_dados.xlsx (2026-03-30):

Peso (g) | Peso com líquido (g) | Valor teórico | Peso água (g) | Volume experimental (µL) | Erro absoluto (µL) | Erro relativo (%)
2.124 | 2.325 | 200 | 0.201 | 201.6048144 | 1.604814443 | 0.8024072217
2.124 | 2.324 | 200 | 0.2 | 200.6018054 | 0.6018054162 | 0.3009027081
2.124 | 2.325 | 200 | 0.201 | 201.6048144 | 1.604814443 | 0.8024072217
2.124 | 2.326 | 200 | 0.202 | 202.6078235 | 2.60782347 | 1.303911735
2.124 | 2.324 | 200 | 0.2 | 200.6018054 | 0.6018054162 | 0.3009027081
2.124 | 2.326 | 200 | 0.202 | 202.6078235 | 2.60782347 | 1.303911735

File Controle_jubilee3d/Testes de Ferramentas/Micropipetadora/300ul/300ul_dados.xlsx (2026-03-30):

Peso (g) | Peso com líquido (g) | Valor teórico | Peso água (g) | Volume experimental (µL) | Erro absoluto (µL) | Erro relativo (%)
2.124 | 2.421 | 300 | 0.297 | 297.893681 | 2.106318957 | 0.702106319
2.124 | 2.424 | 300 | 0.3 | 300.9027081 | 0.9027081244 | 0.3009027081
2.124 | 2.427 | 300 | 0.303 | 303.9117352 | 3.911735206 | 1.303911735
2.124 | 2.422 | 300 | 0.298 | 298.8966901 | 1.10330993 | 0.3677699766
2.124 | 2.422 | 300 | 0.298 | 298.8966901 | 1.10330993 | 0.3677699766
2.124 | 2.423 | 300 | 0.299 | 299.8996991 | 0.1003009027 | 0.03343363424

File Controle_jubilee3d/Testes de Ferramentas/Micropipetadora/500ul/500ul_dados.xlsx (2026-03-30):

Peso (g) | Peso com líquido (g) | Valor teórico | Peso água (g) | Volume experimental (µL) | Erro absoluto (µL) | Erro relativo (%)
2.124 | 2.624 | 500 | 0.5 | 501.5045135 | 1.504513541 | 0.3009027081
2.124 | 2.621 | 500 | 0.497 | 498.4954865 | 1.504513541 | 0.3009027081
2.124 | 2.621 | 500 | 0.497 | 498.4954865 | 1.504513541 | 0.3009027081
2.124 | 2.622 | 500 | 0.498 | 499.4984955 | 0.5015045135 | 0.1003009027
2.124 | 2.622 | 500 | 0.498 | 499.4984955 | 0.5015045135 | 0.1003009027
2.124 | 2.623 | 500 | 0.499 | 500.5015045 | 0.5015045135 | 0.1003009027

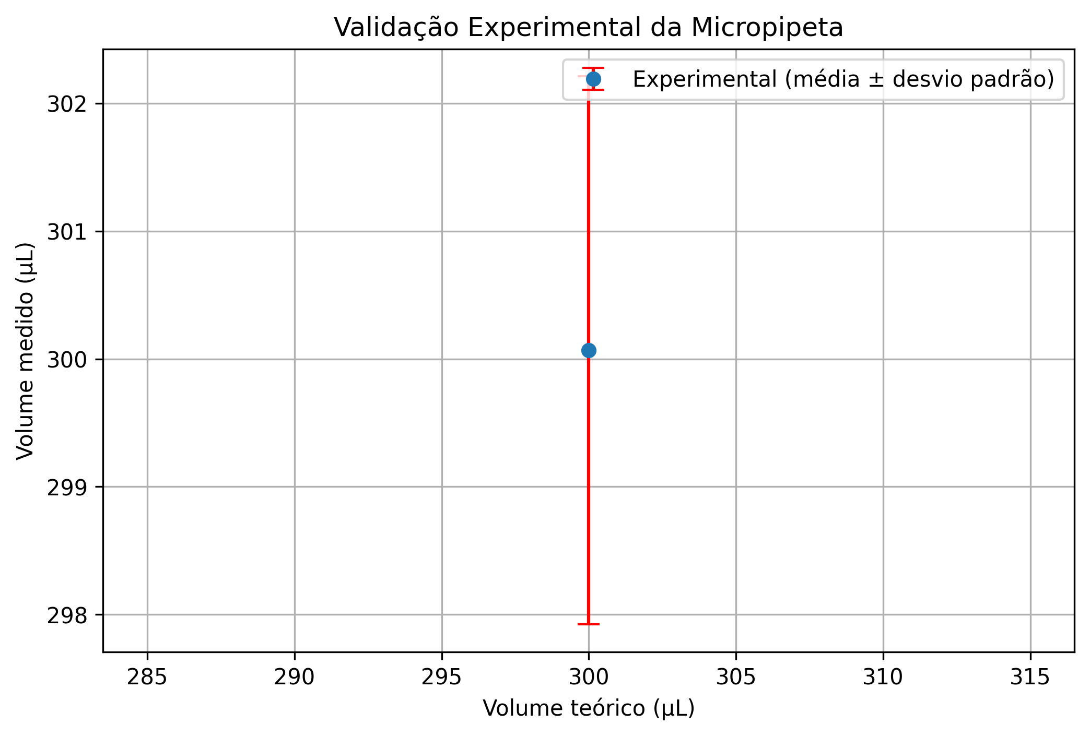
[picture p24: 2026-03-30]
Controle_jubilee3d/Testes de Ferramentas/Micropipetadora/300ul/300ul_grafico.png

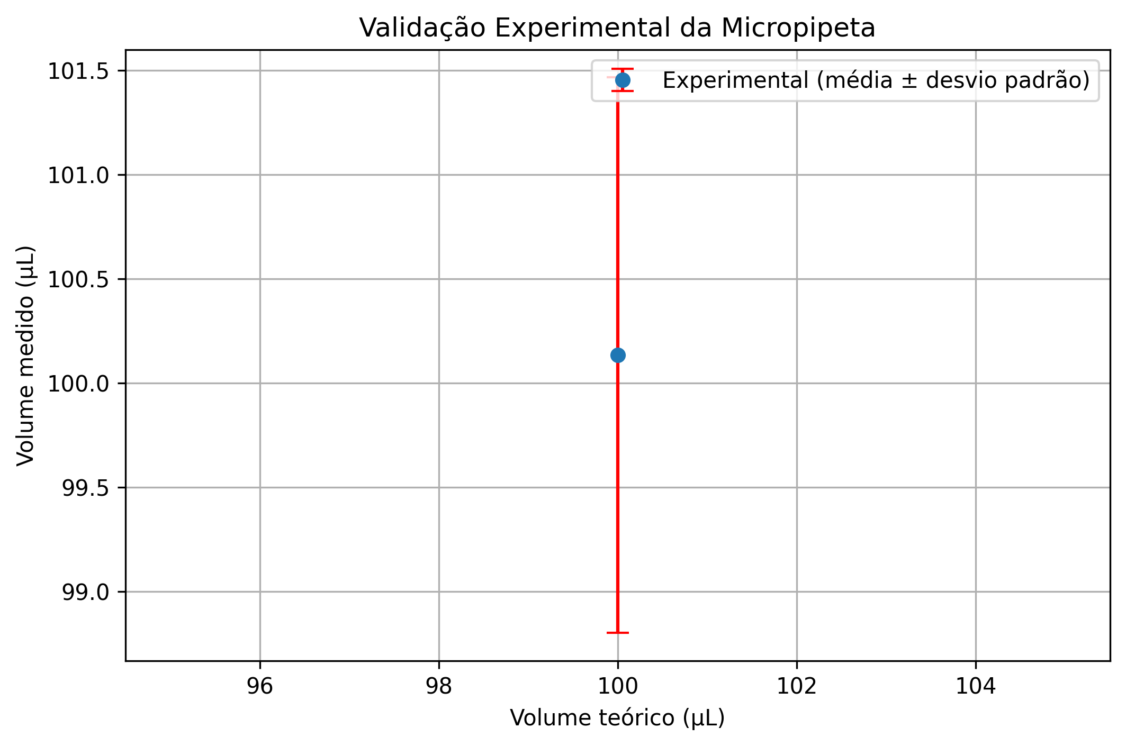
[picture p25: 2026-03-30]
Controle_jubilee3d/Testes de Ferramentas/Micropipetadora/100ul/100ul_grafico.png

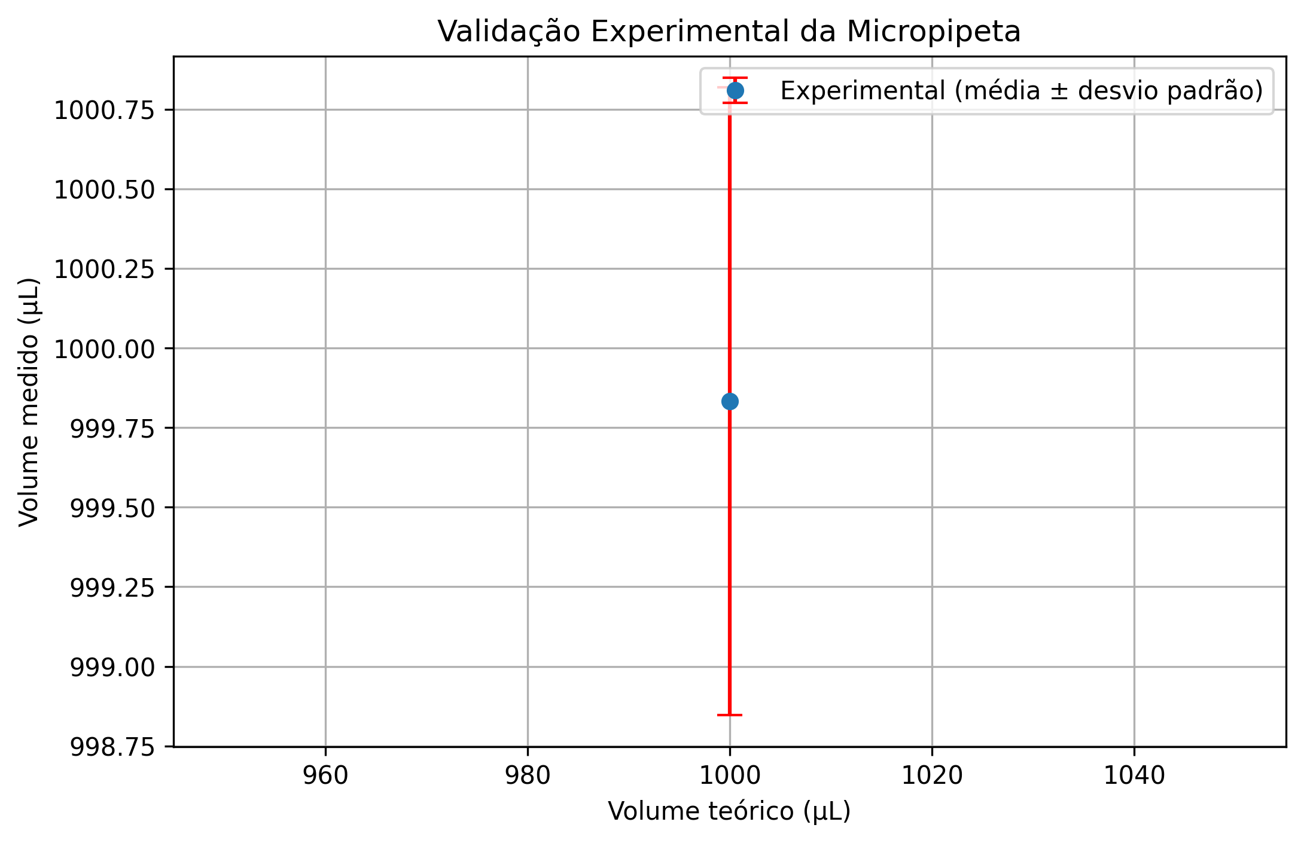
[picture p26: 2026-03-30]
Controle_jubilee3d/Testes de Ferramentas/Micropipetadora/1000ul/1000ul_grafico.png

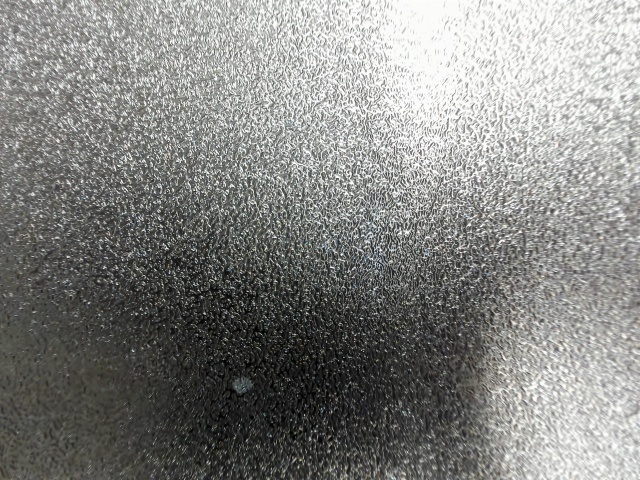
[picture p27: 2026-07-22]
Controle_jubilee3d/Testes de Ferramentas/captura.jpg

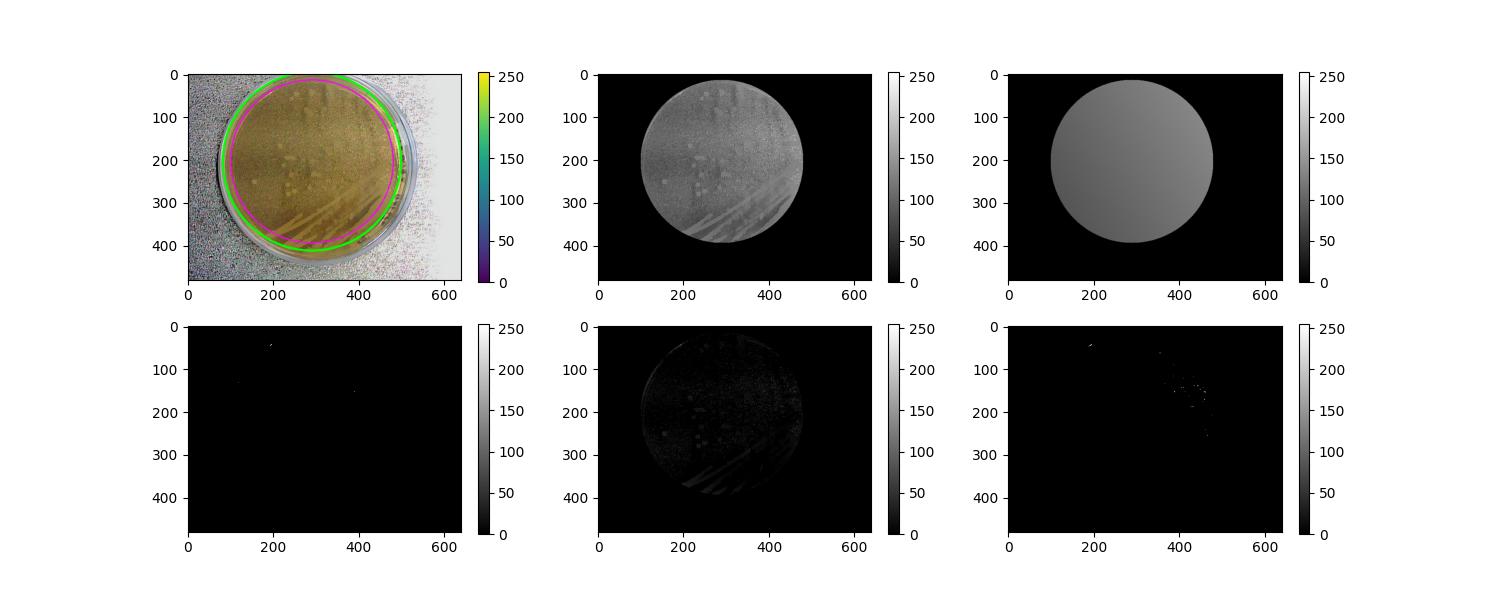
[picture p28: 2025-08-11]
Controle_jubilee3d/Experimento 1 - Crescimento Leveduras/atual_analise placa 2.jpg

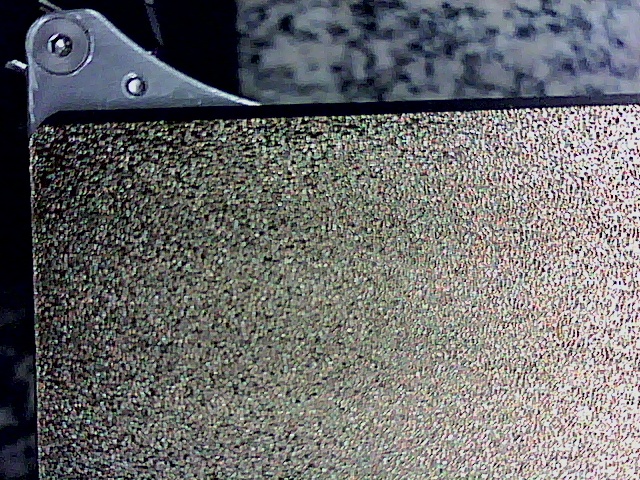
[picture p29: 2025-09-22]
Controle_jubilee3d/Testes de Ferramentas/Micropipetadora/captura.jpg

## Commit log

2025-08-01 processamento de imagem
2025-08-11 experimento 2
    [analise2.xlsx]
2025-09-08 Update README.md
    Correções na estrutura de texto
2025-09-28 Calibração Piepeta, códigos GCode
    [a.xlsx]
2025-10-12 Correções
    [a.xlsx, teste_agora.xlsx]
2025-11-07 Correção pipetadora, dht22, dipcoting e modelos 3d
    [Suporte Ferramenta Micropipetadora.stl, a.xlsx, aaa.xlsx]
2025-11-09 Síntese nanorods
    [1000ul_dados.xlsx, 100ul_dados.xlsx, 120ul_dados.xlsx, 200ul_dados.xlsx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]
2026-03-24 Ajustes de segurança
2026-03-25 Mais informações
    [1000ul_dados.xlsx, 100ul_dados.xlsx, 120ul_dados.xlsx, 200ul_dados.xlsx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]
2026-04-13 Reorganização do teste da ferramenta micropipeta
    [1000ul_dados.xlsx, 100ul_dados.xlsx, 120ul_dados.xlsx, 200ul_dados.xlsx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]
2026-04-13 Novos ajustes
    [geral_dados.xlsx]
2026-04-17 Wedge plate
    [Conector de Eixo.STL]
2026-05-12 Ajuste formatos nomes arquivos para windows
2026-05-13 Eixo w e STl gripper
    [Base_inferior.stl, Base_superior.stl, Gear.stl, Gear2.stl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]
2026-06-11 Correção Diretório e Teste de ferramenta
